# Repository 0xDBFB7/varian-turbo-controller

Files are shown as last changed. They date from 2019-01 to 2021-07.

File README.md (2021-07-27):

This is a small, simple half-bridge circuit that commutates 54 volts into 3-phase at 850 Hz, peak power of about 1 kw for a few minutes, for use with the Varian Turbo-V series of turbomolecular pumps. 

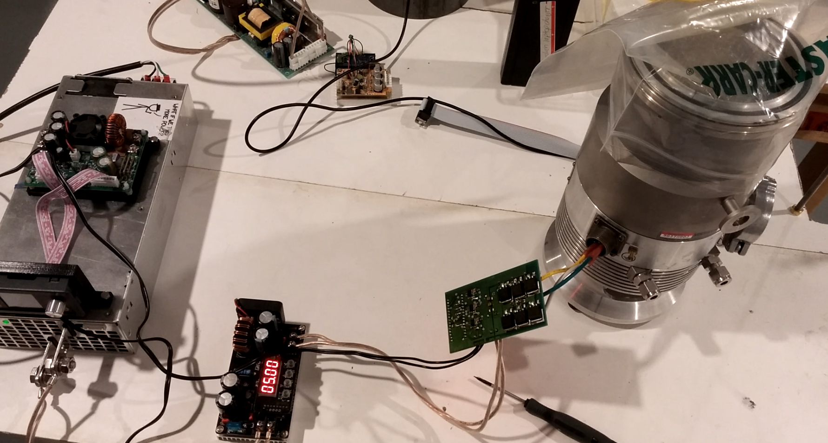
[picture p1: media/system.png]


> WARNING: This board has only been tested for a few hours. The software does not provide any of the sensing or safety features present in the stock controller. It might blow up your pump, kill your cat, spin the earth around your impeller, etc.
>
> Not that I'm a paragon of best practice in any case, but this seriously isn't an acceptable level of quality. In particular, it was designed to be etched at home, as my normal board house was closed for the holidays.
> I've had one instance where shoot-through blew up one of the MOSFETs. I don't know what would happen if this occurs while the pump is at maximum speed. Adding fuseholders between the legs of the half-bridge - and perhaps between each phase to the pump - would probably be a good idea to prevent catastrophic braking.

There are several other open-source turbomolecular pump controller projects online that are better developed and that might be preferable. In addition, the pumps use a kind of synchronous or induction motor, not a "brushless"-like, so no sensing is needed, only a constant 850 Hz, which is basically just a 3-phase VFD or motor controller. Unfortunately, I wasn't able to find any off-the-shelf system with the required parameters.

The circuit is simple enough to easily be built on perfboard. Schematic and bill of materials are [here](files/controller/assembly). The power MOSFETs are BUK9620, with MIC4604YM-TR half-bridge charge-pump drivers.

The input power was supplied by a MeanWell SE-1000-48 with the voltage trimpot adjusted to ~56V, through a DROK Model 200310 10-75V to 0-60V switching buck converter (Amazon), current limit set to about 8A. 

I highly recommend using such a constant-current regulator, because the power supply is extremely powerful - it's practically an arc flash hazard and will easily start a fire.

The MeanWell supply is probably overkill (very expensive), but a cheaper Amazon 48V supply exploded and I didn't want to tempt fate.

I don't know what terminations the turbopump connector uses; crimp butt connectors worked brilliantly.

## [Original Varian controller manual](references/Varian_V200_controller.pdf)

## [Pump manual](references/Varian_V200_turbo_pump.pdf)

### Things that should be added:

If the back-emf sensing is commutated improperly, -5v or so will be put into the sense ADC pins. The integral protection diodes might be okay with that, but probably not. This is disabled at the moment.

More filtering and decoupling should be added. This pump draws nearly 700 watts on startup - there are some massive transients on the power supply rail.

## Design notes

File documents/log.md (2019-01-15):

Project: Varian Turbo
===
Status: In-Progress
-------

#### Date started: 2017-Sep-??
#### Date finished:
#### Date written: 2017-Oct-27

Background:
---

Needed a better vacuum pump for the many experiments I'm running. Tried building my own, but it's just too time intensive. Got a Varian Turbo-V200 from ebay for $220.

Description:
---

This thing says it takes 54v at 850 hz, 3-phase, but I'm not sure if that's "brushless-type" electronically-commutated, or if it's just regular, "3-phase" power. The manual for the controller says it can automatically sync up if the thing's still spinning, which leads me to believe it's doing some commutation. On the other hand, a "rotary" alternator converter can be bought for high-rad environments. IDK.

Because of its unusual power requirements, I wasn't able to find a COTS BLDC controller online that would fit the bill. One board that got close was ST's STEVAL-SPIN3201, which has a nice interface and firmware pre-written et al. However, it only does 45v, and it was $100. Little much.

So, yak shaving recursively, I designed my own board using an attiny84.

I then tried milling it on the Denford. I used a junk-bin engraving bit. I wasn't able to make it route on one layer, so I put four holes in the corners, then cut down a section of precision shaft and pinned the board to a piece of wood mounted on the mill.

Didn't work - kerf on the bit was too high for 20 mil.

Amazon sells a BLDC driver board that I think I can adapt to run at 50v - happens to use the exact same gate driver IC I was going to use. They specify 36v max, looks like an LM317 (37v rated), and 50v caps that I'll swap out. Probably want to hook up an arduino to the sense pin.

Haha, I looked at the seller's pictures and guessed the first four letters of the main IC (interesting blindsight effect!), turns out it uses a JYO1 BLDC controller. Board seems to be exactly the same as a reference one - and it includes schematics.

Got the pump in. $20 BLDC controller didn't work out of the box (didn't kick the blades around enough to catch the EMF for sync), so I hacked in an arduino to the six half-bridge phase pins. Spins up very nicely - makes the most beautiful whine. Little bit of bearing noise. Lathed out a little KF25 to 1/2" npt to 3/8 SAE adapter for the foreline flange, to go to some flared copper.

Some jerk, for reasons unknown, appears to have replaced the standard 1/4" hose barbs with some strange ferruled pipe flange - and then glued them in place with adhesives unknown. Probably going to run with air cooling for now.

Didn't come with oil, spent Sunday looking for oil, seems to be a very light 10 centiStokes@40c grade. Also, can someone please tell the oilluminati to get their measurement standards shit together? There's like 10 different scales. Come on guys, it's oil. Viscocity. Drippiness. Interestingly, the little bit of oil remaining in the pan was quite thick. Impurities? Original oil was just thicker? Degradation? Unsure. The original oil's around $200 for a little bottle, which is pretty steep. Ordered some Boca "HS oil" "Lightning Oil", which has the right weight. IDK.

New pumps seem to use grease / a small amount of oil in a wick.

Now to mate it to my chamber.

Oil came in, needed a second bottle - one just barely enough to charge the oil pan. Looks like the right stuff.

48v power supply came in - I replaced the caps with 80v equivalents and swapped out the LM317 for a high-voltage model.

Contemplated making my own driver again, but OSHpark's shipping fees are insane.

Screw it, I'll run it at 36v.

Nope.

High-side PWM has the advantage of keeping the boost capacitor charged.

Low-side PWM will probably have a lower

Changed phase divider value to 10k to reach TTL levels for fast polling.

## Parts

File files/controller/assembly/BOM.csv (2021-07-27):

Index | Quantity | Part Number | Manufacturer Part Number | Description | Customer Reference | Backorder | Unit Price | Extended Price
1 | 3 | 576-4396-1-ND | MIC4604YM-TR | IC GATE DRVR HALF-BRIDGE 8SOIC |  | 0 | 1.09000 | $3.27
2 | 3 | RHM.005AMCT-ND | PMR18EZPJU5L0 | RES 0.005 OHM 5% 1W 1206 |  | 0 | 0.91000 | $2.73
3 | 20 | RHM2.2KCT-ND | ESR10EZPJ2R2 | RES SMD 2.2 OHM 5% 0.4W 0805 |  | 0 | 0.13000 | $2.60
4 | 2 | 493-1981-ND | UPW2A221MHD | CAP ALUM 220UF 20% 100V RADIAL |  | 0 | 1.46000 | $2.92
5 | 2 | 277-1667-ND | 1935161 | TERM BLK 2POS SIDE ENTRY 5MM PCB |  | 0 | 0.57000 | $1.14
6 | 1 | 277-1578-ND | 1935174 | TERM BLK 3POS SIDE ENTRY 5MM PCB |  | 0 | 0.81000 | $0.81
7 | 5 | HDR100IMP40F-G-RA-TH-ND | HDR100IMP40F-G-RA-TH | CONN HDR 40POS 0.1 GOLD PCB R/A |  | 0 | 1.25000 | $6.25
8 | 6 | 1727-4715-1-ND | BUK9620-100B,118 | MOSFET N-CH 100V 63A D2PAK |  | 0 | 2.39000 | $14.34
11 | 6 | 399-8219-1-ND | C1210C105K1RACTU | CAP CER 1UF 100V X7R 1210 |  | 0 | 1.19000 | $7.14

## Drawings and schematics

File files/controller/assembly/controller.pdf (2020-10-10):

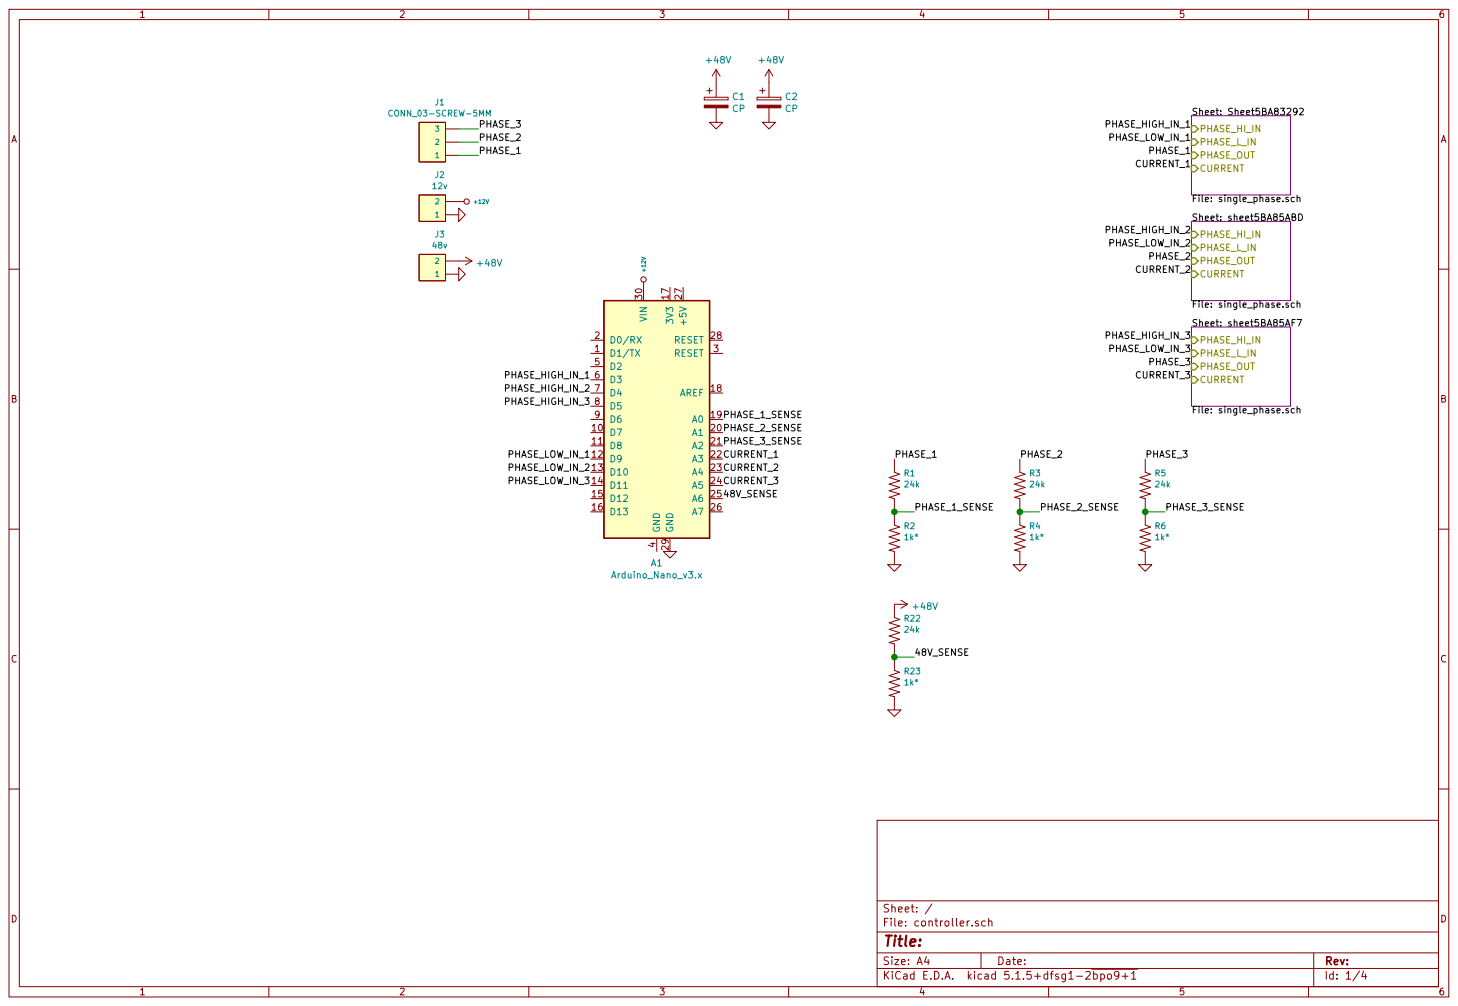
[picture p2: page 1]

PHASE_OUT CURRENT Sheet: Sheet5BA83292 File: single_phase.sch PHASE_HI_IN

Id: 1/4 Title: File: controller.sch Sheet: /

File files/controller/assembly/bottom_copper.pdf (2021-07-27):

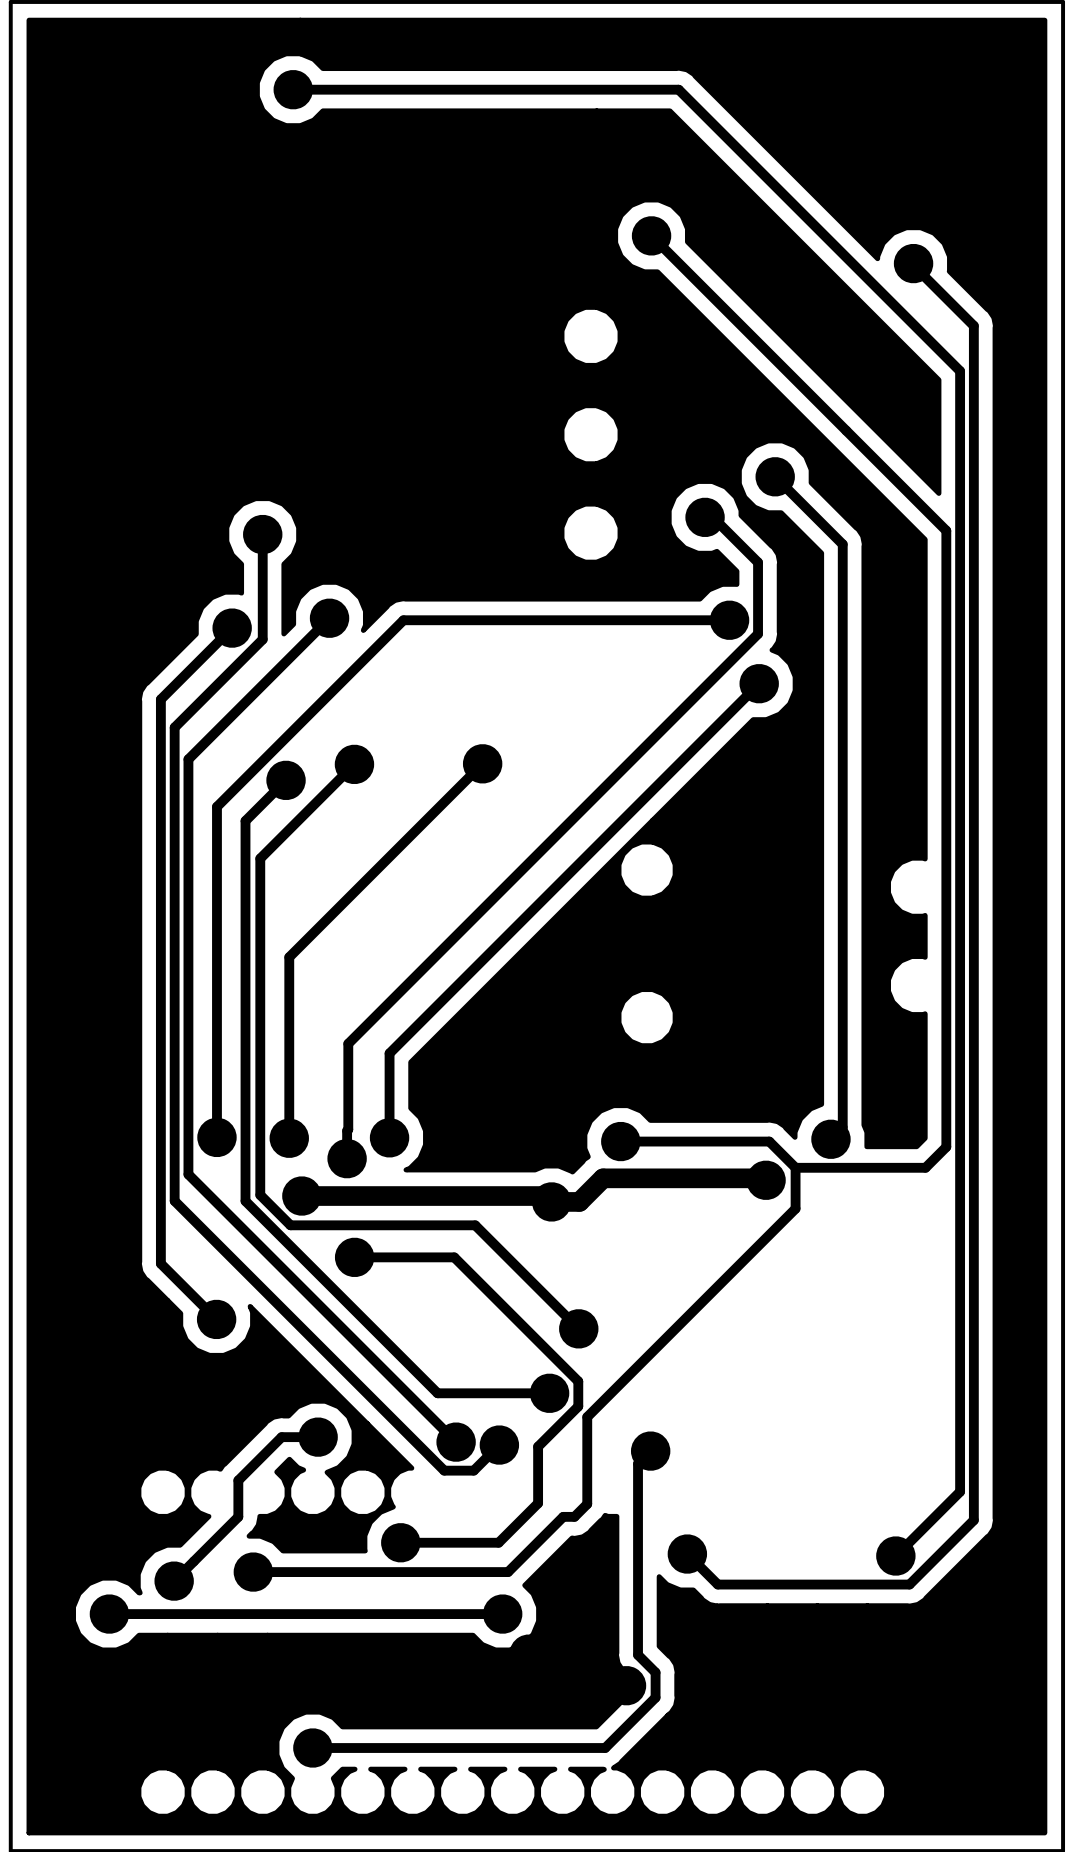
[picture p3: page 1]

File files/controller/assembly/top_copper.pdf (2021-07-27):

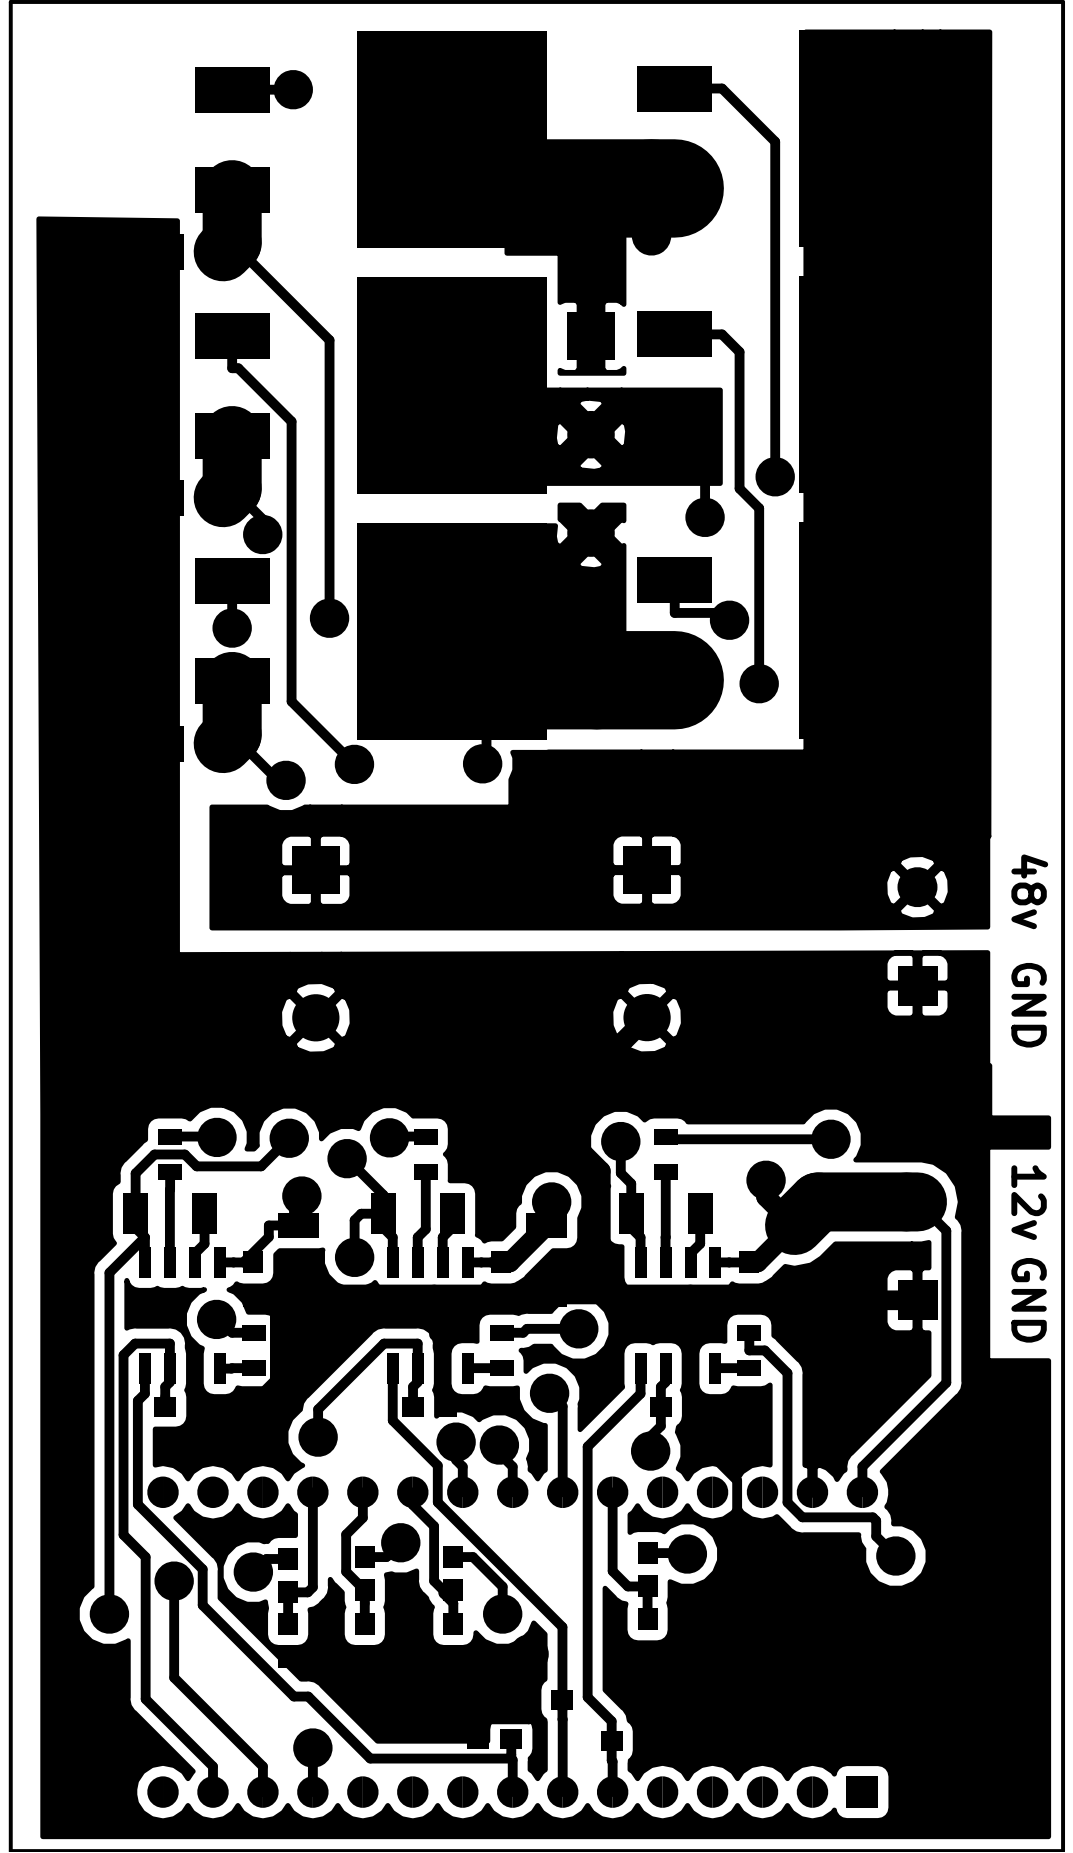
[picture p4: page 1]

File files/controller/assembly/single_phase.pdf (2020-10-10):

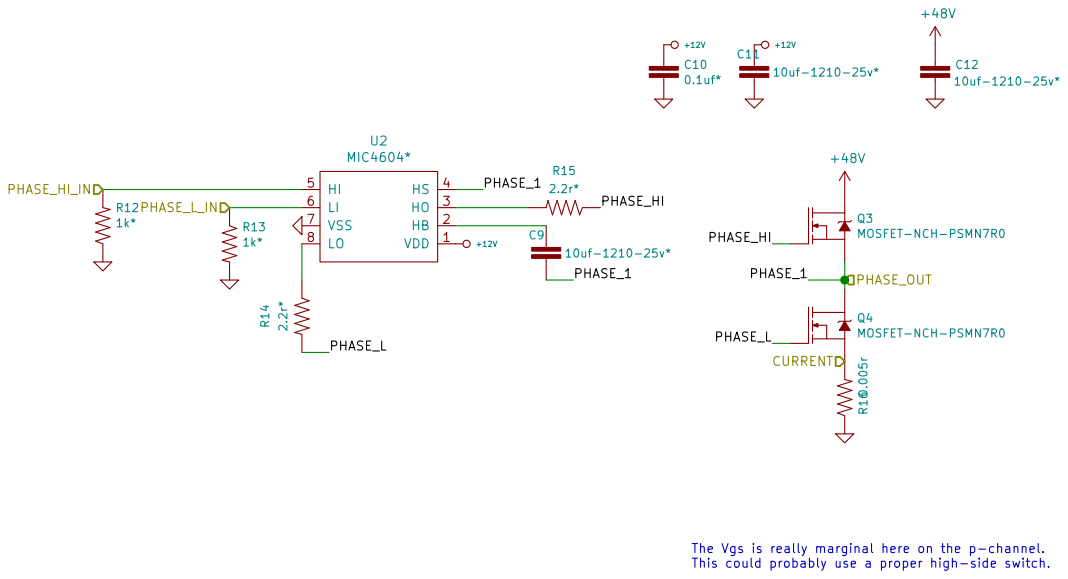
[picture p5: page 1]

This could probably use a proper high-side switch.

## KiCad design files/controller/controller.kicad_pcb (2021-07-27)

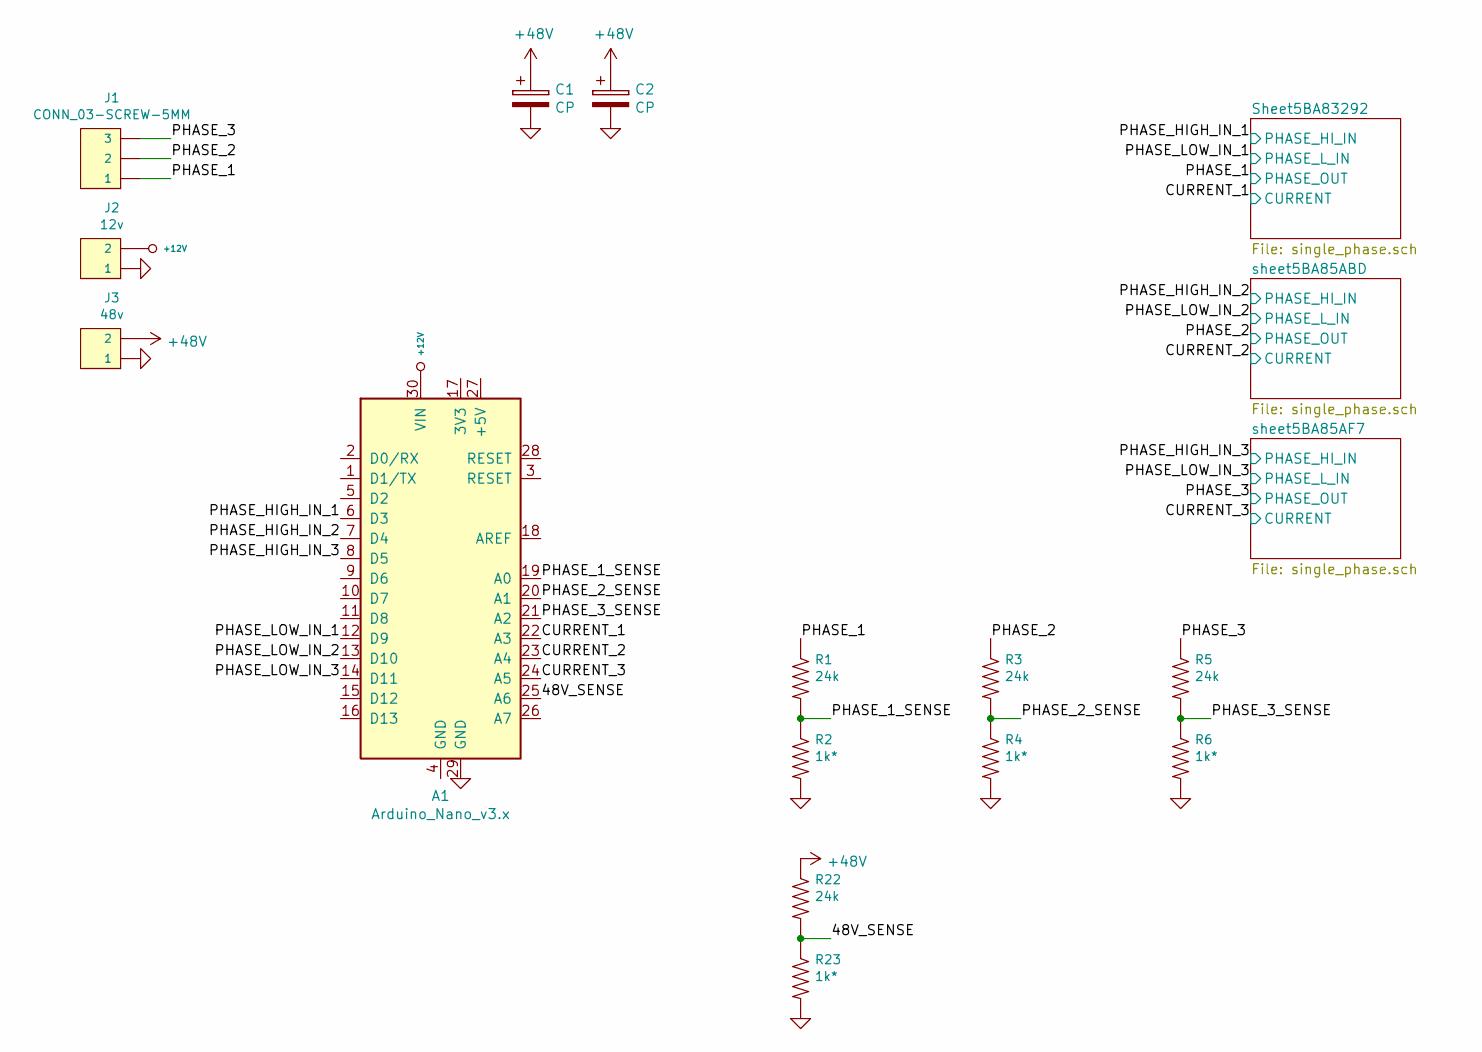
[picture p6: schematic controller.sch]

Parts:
A1: Arduino_Nano_v3.x; Arduino_Nano
C1, C2: CP; CP_Radial_D16.0mm_P7.50mm
J1: CONN_03-SCREW-5MM; SCREWTERMINAL-5MM-3
J2: 12v; SCREWTERMINAL-5MM-2
J3: 48v; SCREWTERMINAL-5MM-2
R1, R3, R5, R22: 24k; 0603
R2, R4, R6, R23: 1k*; 0603

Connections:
+12V: A1.30 (VIN), J2.2; also elsewhere on the board
+48V: C1.1, C2.1, J3.2, R22.1; also elsewhere on the board
/48V_SENSE: A1.25 (A6), R22.2, R23.1
/CURRENT_1: A1.22 (A3); also elsewhere on the board
/CURRENT_2: A1.23 (A4); also elsewhere on the board
/CURRENT_3: A1.24 (A5); also elsewhere on the board
/PHASE_1: J1.1, R1.1; also elsewhere on the board
/PHASE_1_SENSE: A1.19 (A0), R1.2, R2.1
/PHASE_2: J1.2, R3.1; also elsewhere on the board
/PHASE_2_SENSE: A1.20 (A1), R3.2, R4.1
/PHASE_3: J1.3, R5.1; also elsewhere on the board
/PHASE_3_SENSE: A1.21 (A2), R5.2, R6.1
/PHASE_HIGH_IN_1: A1.6 (D3); also elsewhere on the board
/PHASE_HIGH_IN_2: A1.7 (D4); also elsewhere on the board
/PHASE_HIGH_IN_3: A1.8 (D5); also elsewhere on the board
/PHASE_LOW_IN_1: A1.12 (D9); also elsewhere on the board
/PHASE_LOW_IN_2: A1.13 (D10); also elsewhere on the board
/PHASE_LOW_IN_3: A1.14 (D11); also elsewhere on the board
GND: A1.29 (GND), C1.2, C2.2, J2.1, J3.1, R2.2, R4.2, R6.2, R23.2; also elsewhere on the board

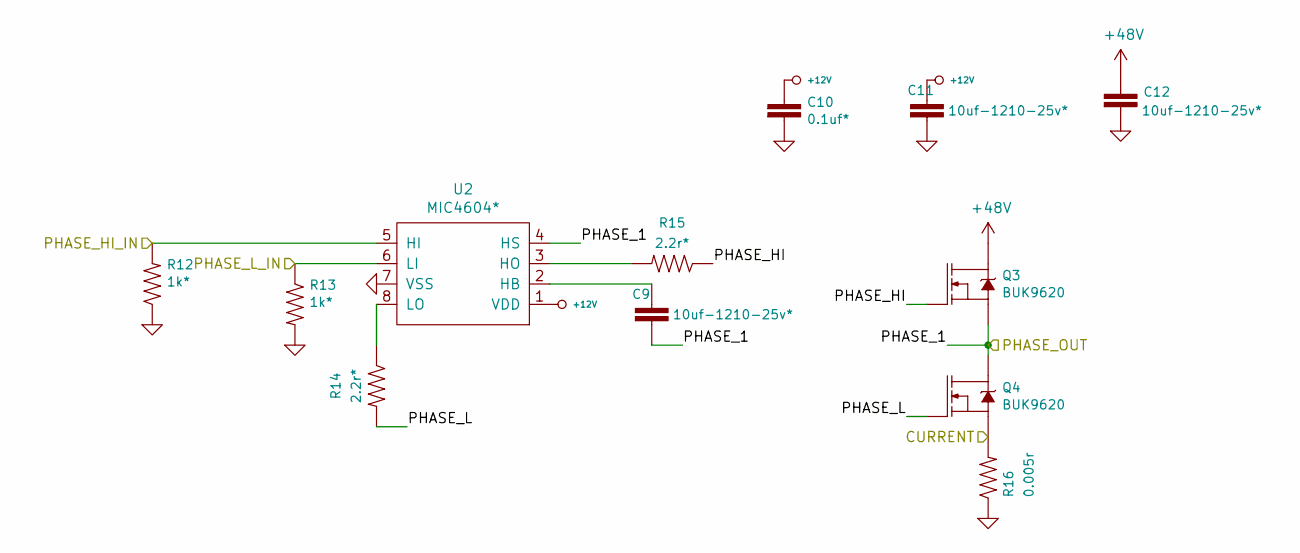
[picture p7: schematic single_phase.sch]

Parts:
C5, C7, C8: 10uf-1210-25v*; 1210
C6: 0.1uf*; 0603
Q1, Q2: BUK9620; TO-263_D2PAK
R7, R8: 1k*; 0603
R9, R10: 2.2r*; 0805
R11: 0.005r; 1206
U1: MIC4604*; SOIC-8_3.9x4.9mm_P1.27mm

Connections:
+12V: C6.1, C7.1, U1.1 (VDD); also elsewhere on the board
+48V: C8.1, Q1.2 (D); also elsewhere on the board
/CURRENT_1: Q2.3 (S), R11.2; also elsewhere on the board
/PHASE_1: C5.2, Q1.3 (S), Q2.2 (D), U1.4 (HS); also elsewhere on the board
/PHASE_HIGH_IN_1: R7.2, U1.5 (HI); also elsewhere on the board
/PHASE_LOW_IN_1: R8.1, U1.6 (LI); also elsewhere on the board
/Sheet5BA83292/PHASE_HI: Q1.1 (G), R10.1
/Sheet5BA83292/PHASE_L: Q2.1 (G), R9.2
GND: C6.2, C7.2, C8.2, R7.1, R8.2, R11.1, U1.7 (VSS); also elsewhere on the board
unnamed: C5.1, U1.2 (HB)
unnamed: R9.1, U1.8 (LO)
unnamed: R10.2, U1.3 (HO)

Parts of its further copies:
C9, C11, C12, C13, C15, C16: 10uf-1210-25v*; 1210
C10, C14: 0.1uf*; 0603
R12, R13, R17, R18: 1k*; 0603
R14, R15, R19, R20: 2.2r*; 0805
R16, R21: 0.005r; 1206
U2, U3: MIC4604*; SOIC-8_3.9x4.9mm_P1.27mm

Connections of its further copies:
+12V: C10.1, C11.1, C14.1, C15.1, U2.1 (VDD), U3.1 (VDD); also elsewhere on the board
+48V: C12.1, C16.1; also elsewhere on the board
/CURRENT_2: R16.2; also elsewhere on the board
/CURRENT_3: R21.2; also elsewhere on the board
/PHASE_2: C9.2, U2.4 (HS); also elsewhere on the board
/PHASE_3: C13.2, U3.4 (HS); also elsewhere on the board
/PHASE_HIGH_IN_2: R12.2, U2.5 (HI); also elsewhere on the board
/PHASE_HIGH_IN_3: R17.2, U3.5 (HI); also elsewhere on the board
/PHASE_LOW_IN_2: R13.1, U2.6 (LI); also elsewhere on the board
/PHASE_LOW_IN_3: R18.1, U3.6 (LI); also elsewhere on the board
/sheet5BA85ABD/PHASE_HI: R15.1; also elsewhere on the board
/sheet5BA85ABD/PHASE_L: R14.2; also elsewhere on the board
/sheet5BA85AF7/PHASE_HI: R20.1; also elsewhere on the board
/sheet5BA85AF7/PHASE_L: R19.2; also elsewhere on the board
GND: C10.2, C11.2, C12.2, C14.2, C15.2, C16.2, R12.1, R13.2, R16.1, R17.1, R18.2, R21.1, U2.7 (VSS), U3.7 (VSS); also elsewhere on the board
unnamed: C9.1, U2.2 (HB)
unnamed: C13.1, U3.2 (HB)
unnamed: R14.1, U2.8 (LO)
unnamed: R15.2, U2.3 (HO)
unnamed: R19.1, U3.8 (LO)
unnamed: R20.2, U3.3 (HO)

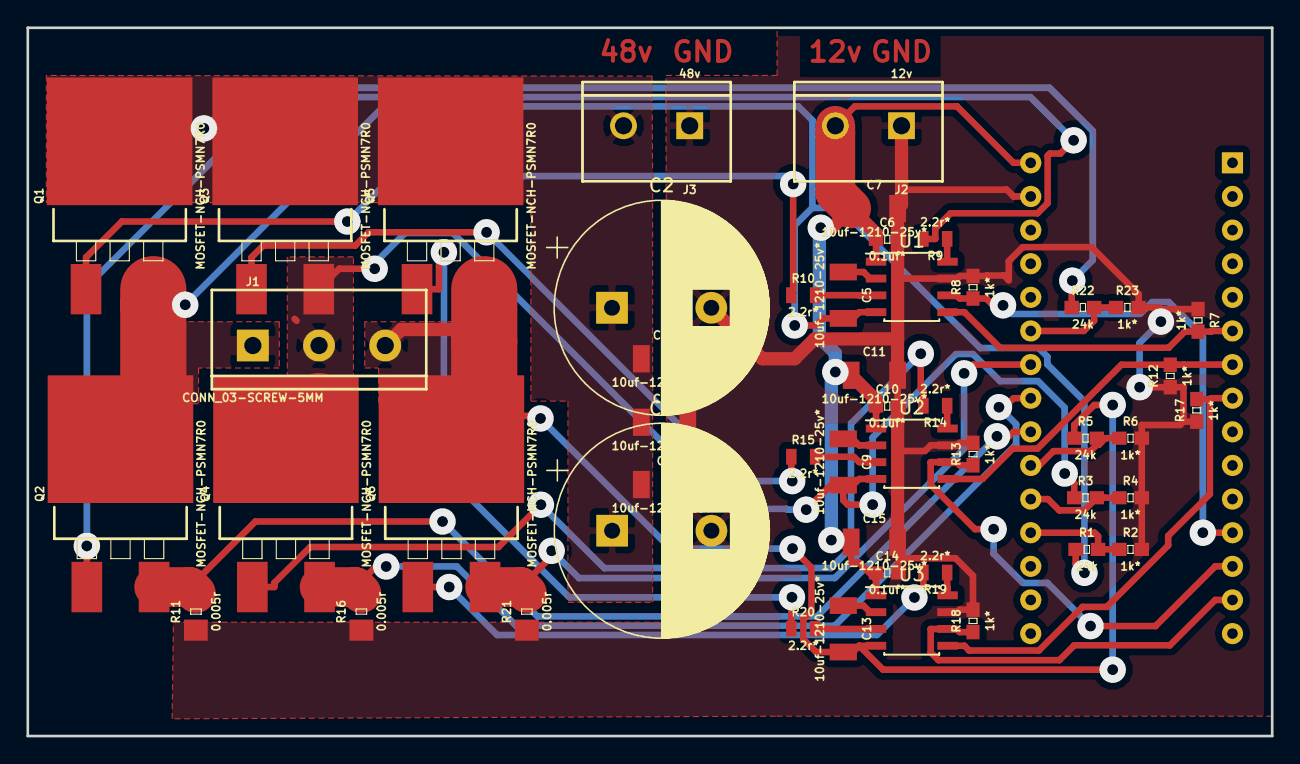
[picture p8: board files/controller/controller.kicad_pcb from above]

Board: 2 copper layers, 94.0 x 53.5 mm, 50 parts (1 on the bottom side), 34 nets.

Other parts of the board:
Q3, Q4, Q5, Q6: MOSFET-NCH-PSMN7R0; TO-263_D2PAK

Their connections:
+48V: Q3.2, Q5.2; also elsewhere on the board
/CURRENT_2: Q4.3; also elsewhere on the board
/CURRENT_3: Q6.3; also elsewhere on the board
/PHASE_2: Q3.3, Q4.2; also elsewhere on the board
/PHASE_3: Q5.3, Q6.2; also elsewhere on the board
/sheet5BA85ABD/PHASE_HI: Q3.1; also elsewhere on the board
/sheet5BA85ABD/PHASE_L: Q4.1; also elsewhere on the board
/sheet5BA85AF7/PHASE_HI: Q5.1; also elsewhere on the board
/sheet5BA85AF7/PHASE_L: Q6.1; also elsewhere on the board

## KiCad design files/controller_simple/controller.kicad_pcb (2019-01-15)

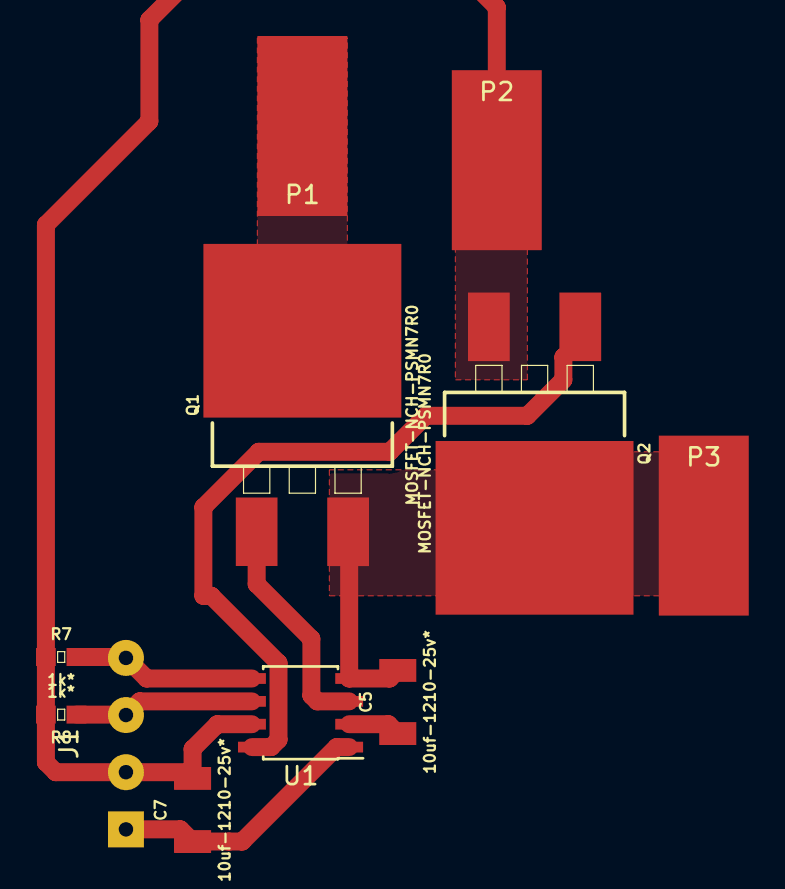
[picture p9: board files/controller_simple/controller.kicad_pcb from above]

Board: 2 copper layers, 11 parts (0 on the bottom side), 9 nets.

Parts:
C5, C7: 10uf-1210-25v*; 1210
J1: CONN_04SMD_LONG; SolderWirePad_1x04_P3.175mm_Drill0.8mm
P1, P2, P3: CONN_1; SolderWirePad_1x01_SMD_5x10mm
Q1, Q2: MOSFET-NCH-PSMN7R0; TO-263_D2PAK
R7, R8: 1k*; 0603
U1: MIC4604*; SOIC-8_3.9x4.9mm_P1.27mm

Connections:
+12V: C7.1, J1.1, U1.1
+48V: P1.1, Q1.2
/PHASE_HIGH_IN_1: J1.4, R7.2, U1.5
/PHASE_LOW_IN_1: J1.3, R8.1, U1.6
/Sheet5BA83292/PHASE_HI: Q1.1, U1.3
/Sheet5BA83292/PHASE_L: Q2.1, U1.8
/Sheet5BA83292/PHASE_OUT: C5.2, P3.1, Q1.3, Q2.2, U1.4
GND: C7.2, J1.2, P2.1, Q2.3, R7.1, R8.2, U1.7
unnamed: C5.1, U1.2

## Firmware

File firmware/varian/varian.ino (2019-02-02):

#include <digitalWriteFast.h>

#define A_H 3 
#define A_L 9
#define B_H 4
#define B_L 10
#define C_H 5
#define C_L 11

#define AC_FREQ 850
#define SHOOT_THROUGH_DWELL 1 //microsecond
#define PWM_TWEAK 76 //microseconds - this could be alleviated via direct T/C register manipulation,
                     //but I couldn't be bothered.
#define RAMP_SPEED 60

void actuate_phase(bool state, int duty, int high_pin, int low_pin){
  if(state){
    digitalWriteFast(low_pin,0);
    delayMicroseconds(SHOOT_THROUGH_DWELL);
    digitalWriteFast(high_pin,1);
  }
  else{
    digitalWriteFast(high_pin,0);
    delayMicroseconds(SHOOT_THROUGH_DWELL);
    digitalWriteFast(low_pin,1);
  }
}

void phase_1(bool state, int duty){
  actuate_phase(state, duty, A_H, A_L);
}

void phase_2(bool state, int duty){
  actuate_phase(state, duty, B_H, B_L);
}

void phase_3(bool state, int duty){
  actuate_phase(state, duty, C_H, C_L);
}

void highz_phase(){
  digitalWriteFast(A_H,0);
  digitalWriteFast(A_L,0);
  digitalWriteFast(B_H,0);
  digitalWriteFast(B_L,1);
  digitalWriteFast(C_H,0);
  digitalWriteFast(C_L,0);
}

void setup() {
//  TCCR1B = TCCR1B & 0b11111000 | 2; //Switch to 31khz PWM 
//  TCCR2B = TCCR2B & 0b11111000 | 2;
  Serial.begin(115200);
  pinMode(A_H,OUTPUT);
  pinMode(A_L,OUTPUT);
  pinMode(B_H,OUTPUT);
  pinMode(B_L,OUTPUT);
  pinMode(C_H,OUTPUT);
  pinMode(C_L,OUTPUT);
}


void loop() {
  int current_speed = 0;
  int total = (((1.0/AC_FREQ)*1e6)-SHOOT_THROUGH_DWELL)/6.0;

  while(true){
    for(int i = 0; i < AC_FREQ/10; i++){ 
      phase_1(1,current_speed);
      delayMicroseconds(total);
      phase_3(0,current_speed);
      delayMicroseconds(total);
      phase_2(1,current_speed);
      delayMicroseconds(total);
      phase_1(0,current_speed);
      delayMicroseconds(total);
      phase_3(1,current_speed);
      delayMicroseconds(total);
      phase_2(0,current_speed);
      delayMicroseconds(total);
    }
    
    current_speed=100;
    //current_speed = constrain(current_speed,0,100);
    //highz_phase();
    //long pulse_time = pulseIn(A0,0,100);
  }
}

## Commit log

2019-02-02 Removed some references, added firmware
    [controller-F.Cu.gbr, controller.drl, controller.dsn, controller.kicad_pcb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]
2021-07-27 Cleaned up text
    [BOM.csv]
2021-07-27 Changed component names
    [2017-10-08T22-46-43.csv, controller-F.Cu.gbr, controller.drl, controller.dsn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]
